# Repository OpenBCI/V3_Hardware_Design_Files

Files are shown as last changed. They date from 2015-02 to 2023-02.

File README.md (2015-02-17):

# V3_Hardware_Design_Files
Contains files created with Design Spark PCB Capture Software

# Installation
Design Spark is a free PCB design software available for download here
http://www.rs-online.com/designspark/electronics/eng/page/designspark-pcb-home-page

Download and install the Design Spark software (Windows based), then follow the instructions below to view, modify, etc.

The OpenBCI board suite uses many custom components that we've designed in Design Spark.
In order to use the design files to their fullest extent, you must add the files contained in the Design Spark Libraries folder to the following location:

    Users\Public\Documents\DesignSpark PCB 7.0\Library\User

Then, fire up Design Spark! If this is your first time running Design Spark, you will need to enable the Library folder first thing. When Design Spark opens, open the Libraries pane by clicking File, Libraries (Cntrl+L). When it opens, click on the Folders tab and select 

    C:\Users\Public\Documents\DesignSpark PCB 7.0\Library 

Then click the 'Folder Enebled' radio button.

Now when you open the .sch and .pcb files, you can modify to your hearts delight!

# License Information

All contents of this repository are released under [Creative Commons Share-alike 3.0](http://creativecommons.org/licenses/by-sa/3.0/).

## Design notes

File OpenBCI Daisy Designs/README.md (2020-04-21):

# OpenBCI Daisy Hardware Design Files

You should have received a copy of the license information for these Open Source hardware files. We are licensing under the [CC-BY-SA 4.0 License](http://creativecommons.org/licenses/by-sa/4.0/legalcode). You should also have downloaded the Design Spark Library files in this directories parent. To get setup with the Design Spark software, go [here.](https://github.com/OpenBCI/V3_Hardware_Design_Files/blob/master/README.md)

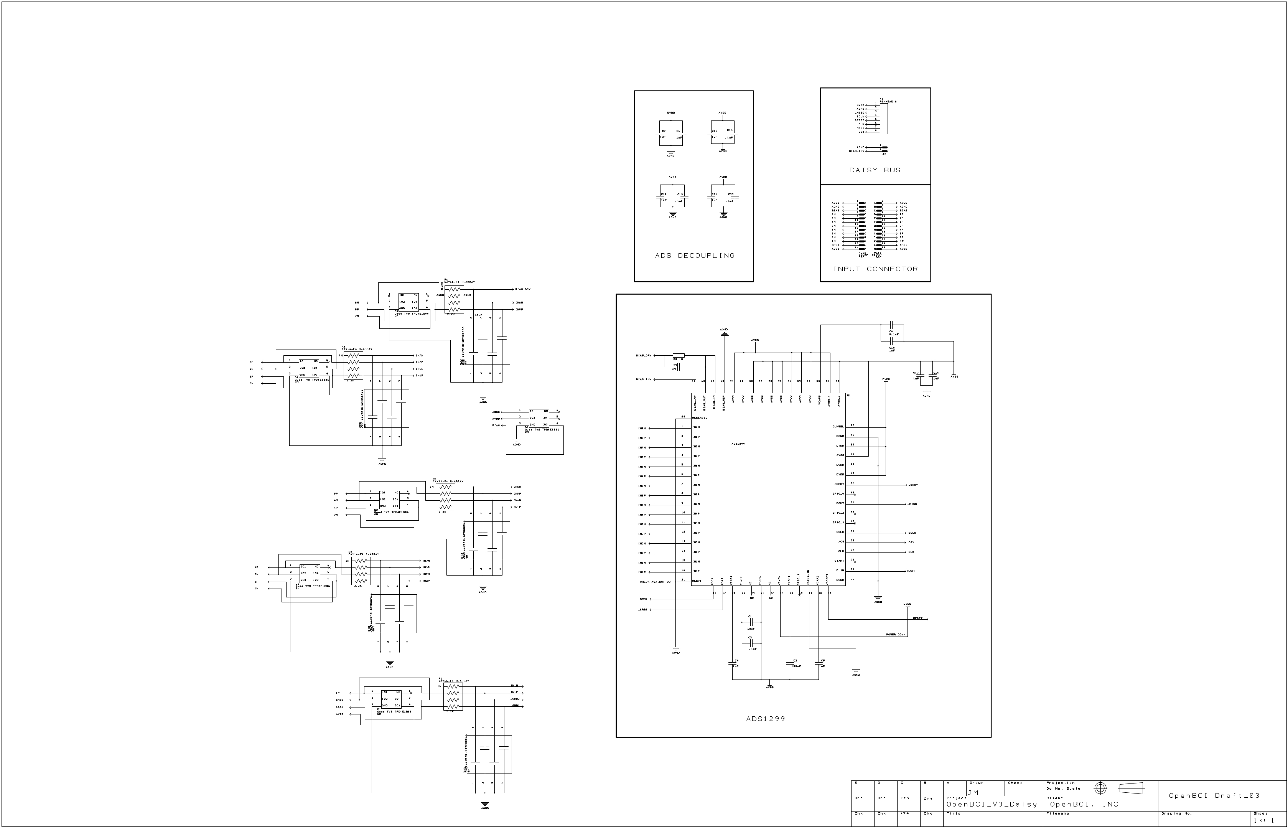
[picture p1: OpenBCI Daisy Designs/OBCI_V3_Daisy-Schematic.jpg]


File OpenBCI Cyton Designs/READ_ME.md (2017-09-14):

# OpenBCI Cyton Hardware Design Files

**NOTE** The OpenBCI **Cyton** used to be called the **32bit Board**. It has be rebranded and there is NO difference between the two.

You should have received a copy of the license information for these Open Source hardware files. We are licensing under the [CC-BY-SA 4.0 License](http://creativecommons.org/licenses/by-sa/4.0/legalcode). You should also have downloaded the Design Spark Library files in this directories parent. To get setup with the Design Spark software, go [here.](https://github.com/OpenBCI/V3_Hardware_Design_Files/blob/master/README.md)

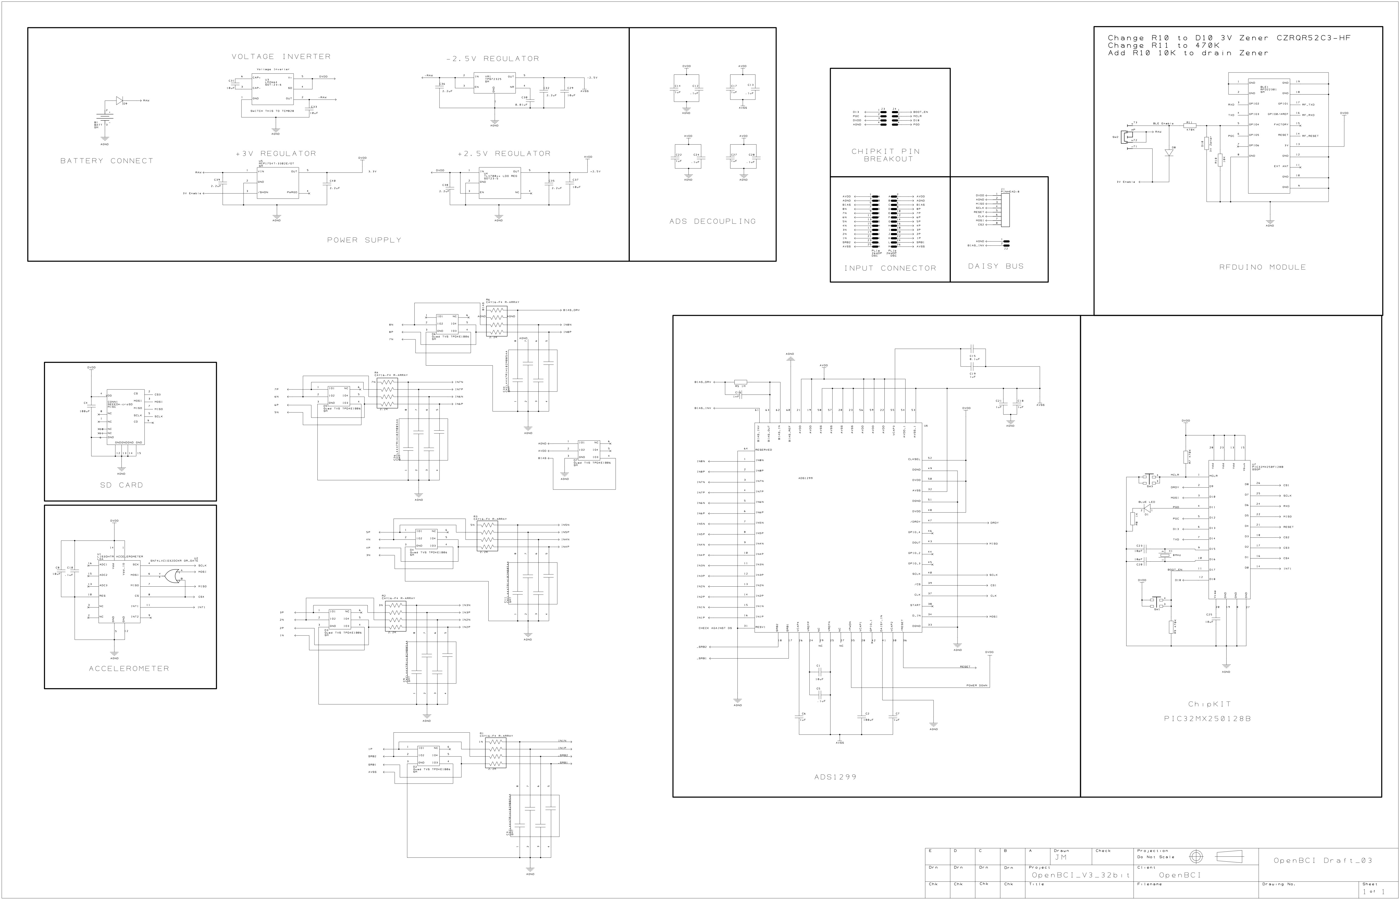
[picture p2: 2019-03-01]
OpenBCI Cyton Designs/OBCI_V3_32bit-Schematic.jpg

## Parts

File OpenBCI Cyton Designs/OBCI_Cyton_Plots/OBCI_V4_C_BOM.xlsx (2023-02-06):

 | OBCI_V3_C
Item | Board Ref | Qty | Component | Value | Package | Manufacturer | Part Number | Description
1 | C2,C4 | 2 | C | 100uF | SM 1206 | Yageo | CC1206MKX5R5BB107 | MLCC
2 | C1,C8,C25,C29,C31,C33,C37 | 7 | C | 10uF | SM0603 | Murata | GRM188C80G106KE47D | MLCC
3 | C32,C35,C36,C38,C40 | 5 | C | 2.2uF | EIA_0402 | Murata | GRM155C80J225ME95D | MLCC
4 | C39 | 1 | C | 2.2uF | EIA_0402 | Murata | GRM155R61C225KE44D | MLCC
5 | C6,C7,C14,C17,C18,C19,C21,C22,C27 | 9 | C | 1uF | EIA_0402 | Yageo | CC0402KRX7R5BB105 | MLCC
6 | C5,C10,C12,C13,C15,C24,C28 | 7 | C | 0.1uF | EIA_0402 | Yageo | CC0402KRX7R7BB104 | MLCC
7 | C30 | 1 | C | 0.01uF | EIA_0402 | Yageo | CC0402KRX7R7BB103 | MLCC
8 | C16 | 1 | C | 0.001uF | EIA_0402 | Yageo | CC0402KRX7R7BB102 | MLCC
9 | C20,C23 | 2 | C | 18pF | EIA_0402 | Yageo | CC0402JRNPO9BN180 | MLCC
10 | R1,R2,R3,R4,R6 | 5 | R | 2.2K | SM | BOURNS | CAY16-2201F4LF | 4 R-ARRAY
11 | C3,C9,C11,C26,C34 | 5 | C | 0.001uF | SM | TDK | CKCL44X7R1H102M085AA | 4 CAP ARRAY
12 | U1 | 1 | U |  | LGA | ST | LIS3DHTR | ST ACCELEROMETER
13 | U2 | 1 | U |  | SM | TI | SN74LVC1G32DCKR | OR_GATE
14 | U3 | 1 | U |  | SOT-23-6 | TI | LM2664M6/NOPB | V INVERTER
15 | U4 | 1 | U |  | SOT-23-5 | TI | TLV70025QDDCRQ1 | +2.5V LDO REG
16 | U5 | 1 | U |  | SM | Microchip | MCP1754T-3302E/OT | 3V3 LDO REG
17 | U6 | 1 | U |  | TQFP-64 | TI | ADS1299IPAG | ADS1299
18 | U7 | 1 | U |  | SSOP-28 | Microchip | PIC32MX250F128B-I/SS | PIC32 MICROCONTROLLER
19 | VR1 | 1 | VR |  | SM | TI | TPS72325DBVR | -2.5 LDO REG
20 | BLE1 | 1 | BLE |  | SM | RF DIGITAL | RFD22301 | BTLE Module
21 | D1 | 1 | D | LED | SM 0603 | Lite-On | LTST-C193TBKT-5A | BLUE LED
22 | D8 | 2 | D |  | SM 0603 | Comchip | CDSU400B | DIODE
23 | D9 | 1 | D |  | SM 0603 | Comchip | CDBU0130L | DIODE
24 | D2,D3,D4,D5,D6,D7 | 6 | D |  | SM | TI | TPD4E1B06DCKR | TI QUAD TVS
25 | D10 | 1 | D | 3V | SOD-923 | Comchip | CZRQR52C3-HF | 3V Zener Diode
26 | R8,R10,R11 | 3 | R | 1K | EIA_0402 | Yageo | RT0402FRE071KL | Resistor
27 | R5 | 1 | R | 1M | EIA_0402 | Yageo | RC0402JR-071ML | Resistor
28 | R7,R9 | 2 | R | 470K | EIA_0402 | Yageo | RC0402JR-07470KL | Resistor
29 | X1 | 1 | X | 8MHz | SM | ABRACON | ABMM2-8.000MHZ-E2-T | 8MHz XTAL
30 | B1 | 1 | BATT |  | SM | JST Sales | S2B-PH-SM4-TB(LF)(SN) | CONN HEADER PH SIDE 2POS 2MM SMD
31 | SW2 | 1 | S |  | SM | COPAL | CUS-13TB | SP3T SLIDE SWITCH
32 | SW1,SW3 | 2 | S |  | SM | C&K | PTS810 SJK 250 SMTR LFS | TACT SWITCH
33 | CONN1 | 1 | CONN |  | SM | SUNTECH | ST-TF-003A | microSD card slot
34 | PL1 | 1 | J |  | DIP | Wurth | 61302221021 | Dual 11 x 2 0.1" pitch MALE header row Right Angle

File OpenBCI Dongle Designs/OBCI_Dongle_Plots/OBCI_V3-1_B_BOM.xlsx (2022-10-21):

 | OBCI_V3_B
Item | Board Ref | Qty | Component | Value | Package | Manufacturer | Part Number | Description
1 | U1 | 1 | FT231X |  | QFN-20 | FTDI | FT231XQ-R | FTDI VCP
2 | BLE1 | 1 | Rfduino |  | SM | Rfdigital | RFD22301 | BTLE Module
3 | D1,D2 | 2 | ESD_VARISTOR |  | SM_0402 | BOURNS | CG0402MLC-05LG | tsv varistor
4 | D3 | 1 | TVS_D |  | SOD882 | ST | ESDALC6V1-1M2 | transient suppressor
5 | D6 | 1 | SMT_LED | BLUE | SM_0603 | Lite-On | LTST-C193TBKT-5A | BLUE LED
6 | D5 | 1 | SMT_LED | GREEN | SM_0603 | Lite-On | LTST-C191KGKT | GREEN LED
7 | D4 | 1 | SMT_LED | RED | SM_0603 | Lite-On | LTST-C191KRKT | RED LED
8 | L1,L2 | 2 | CHOKE |  | SM_0402 | TDK | MPZ1005S300C | FERRITE CHIP
9 | F1 | 1 | SM_FUSE |  | SM_1812 | BOURNS | MF-MSMF050-2 | FUSE
10 | R6,R7 | 2 | R 0402 | 1K | EIA_0402 | Yageo | RT0402FRE071KL | CHIP RESISTOR
11 | R1,R2 | 2 | R 0402 | 22 Ohm | EIA_0402 | Yageo | RC0402FR-0722RL | CHIP RESISTOR
12 | R3,R4,R5 | 3 | R 0402 | 330 Ohm | SM_0402 | Yageo | RC0402JR-07330RL | CHIP RESISTOR
13 | C1,C5, C6 | 3 | C | 0.01uF | EIA_0402 | Yageo | CC0402KRX7R7BB103 | MLCC X7R
14 | C2,C3 | 2 | C | 47pF | SM_0402 | Murata | GRM0335C1E470JA01D | MLCC X7R
15 | C4 | 1 | C 10uF | 10uF | SM0603 | Murata | GRM188C80G106KE47D | MLCC X7R
16 | S1 | 1 | SMT_SPDT_Switch |  | SM | ALPS | SSSS811101 | SPDT SLIDE SWITCH
17 | R8, R9 | 2 | R 0402 | 10K | SM_0402 | Yageo | RC0402JR-07330RL | CHIP RESISTOR

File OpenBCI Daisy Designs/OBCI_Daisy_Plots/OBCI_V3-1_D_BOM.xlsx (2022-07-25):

 | OBCI_V3_D
Item | Board Reference | Qty | Component | Value | Package | Manufacturer | Part Number | Description
1 | U1 | 1 | U |  | TQFP-64 | TI | ADS1299IPAG | ADS1299
2 | D1,D2,D3,D4,D5,D6 | 6 | D |  | SM | TI | TPD4E1B06DCKR | QUAD TVS
3 | C2 | 1 | C | 100uF | SM 1206 | Yageo | CC1206MKX5R5BB107 | Capacitor, Surface Mount Multi-Layer Ceramic
4 | C1 | 1 | C | 10uF | SM0603 | Murata | GRM188C80G106KE47D | Capacitor, Surface Mount Multi-Layer Ceramic
5 | C3,C6,C8,C14,C19,C22 | 6 | C | 0.1uF | EIA_0402 | Yageo | CC0402KRX7R7BB104 | Capacitor, Surface Mount Multi-Layer Ceramic
6 | C9 | 1 | C | 0.001uF | EIA_0402 | Yageo | CC0402KRX7R7BB102 | Capacitor, Surface Mount Multi-Layer Ceramic
7 | C4,C5,C7,C10,C15,C16,C17,C18,C21 | 9 | C | 1uF | EIA_0402 | Yageo | CC0402KRX7R5BB105 | Capacitor, Surface Mount Multi-Layer Ceramic
8 | C11,C12,C13,C20,C23 | 5 | C | 0.001uF | SM | TDK | CKCL44X7R1H102M085AA | 4 CAPACITOR ARRAY
9 | R1,R2,R3,R4,R6 | 5 | R | 2.2K | SM | BOURNS | CAY16-2201F4LF | 4 R-ARRAY
10 | R5 | 1 | R | 1M | EIA_0402 | Yageo | RC0402JR-071ML | Resistor
11 | PL1 | 1 | J |  | DIP | Wurth | 61302221021 | Dual 11 x 2 0.1" pitch MALE header row Right Angle

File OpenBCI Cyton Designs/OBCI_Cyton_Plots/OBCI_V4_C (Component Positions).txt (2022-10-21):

Component Positions Report
--------------------------

Report File:    C:\Users\murf\Documents\SPARK\ADS_EEG\ADS_V3_BT\OBCI_C\OBCI_V4_C (Component Positions).txt
Report Written: Friday, August 12, 2016
Design Path:    C:\Users\murf\Documents\SPARK\ADS_EEG\ADS_V3_BT\OBCI_C\OBCI_V4_C.pcb
Design Title:
Created:        7/30/2013 10:43:11 PM
Last Saved:     8/12/2016 11:11:35 AM
Editing Time:   116245 min
Units:          thou (precision 0)

Name      Component                     Side                    Centre X    Centre Y  Rotation
----------------------------------------------------------------------------------------------
J2        2WP                           Top                         1611        1483    180.00
J3        4WP                           Top                         1912         375    315.00
J4        4WP                           Top                         2104         739      0.00
PL1       26WDP                         Top                         1217        2119    270.00
C1        0603YC104KATDA                Top                          784        1422    270.00
C8        0603YC104KATDA                Top                          881         174    180.00
C25       0603YC104KATDA                Bottom                      1251         870     90.00
C29       0603YC104KATDA                Bottom                      1373        1138    270.00
C31       06033G104ZATDA                Bottom                      1349         768    180.00
C33       06033G104ZATDA                Bottom                      1464         921    270.00
X1        ABRACON_XTAL                  Top                         1672         795    270.00
U6        ADS1299                       Top                         1172        1403    270.00
B1        BATT                          Bottom                      1993        1477    180.00
C5        C                             Top                          873        1433    180.00
C6        C                             Top                          846        1370    270.00
C7        C                             Top                          846        1236    270.00
C10       C                             Top                          941         186    180.00
C12       C                             Top                         1351        1108     90.00
C13       C                             Bottom                      1125        1450      0.00
C14       C                             Top                         1351        1068     90.00
C15       C                             Top                         1473        1404      0.00
C16       C                             Top                         1508        1550      0.00
C17       C                             Bottom                      1163        1450      0.00
C18       C                             Bottom                      1181        1386    270.00
C19       C                             Top                         1509        1404      0.00
C20       C                             Top                         1646         949     90.00
C21       C                             Bottom                      1181        1348    270.00
C22       C                             Bottom                      1201        1450      0.00
C23       C                             Top                         1700         643    270.00
C24       C                             Bottom                      1239        1450      0.00
C27       C                             Bottom                      1299        1430    270.00
C28       C                             Bottom                      1299        1392    270.00
C30       C                             Bottom                      1356         923     90.00
C32       C                             Bottom                      1480        1128     90.00
C35       C                             Bottom                      1561        1127    270.00
C36       C                             Bottom                      1560        1042    180.00
C38       C                             Bottom                      1830        1092      0.00
C39       C                             Bottom                      1917        1006     90.00
C40       C                             Bottom                      1916         758     90.00
C37       C 10uF                        Bottom                      1618        1186    270.00
C2        C 100uF                       Top                          771        1307     90.00
C4        C 100uF                       Bottom                       789         196    315.00
R1        CAY16-F4 R-ARRAY              Top                          796        1843    180.00
R2        CAY16-F4 R-ARRAY              Top                          988        1842    180.00
R3        CAY16-F4 R-ARRAY              Top                         1180        1843    180.00
R4        CAY16-F4 R-ARRAY              Top                         1372        1842    180.00
R6        CAY16-F4 R-ARRAY              Top                         1566        1842    180.00
LOGO1     CHIPKIT                       Top                         1414         454      0.00
C3        CKCL44X7R1H102M085AA          Bottom                       794        1645      0.00
C9        CKCL44X7R1H102M085AA          Bottom                       998        1645      0.00
C11       CKCL44X7R1H102M085AA          Bottom                      1176        1645      0.00
C26       CKCL44X7R1H102M085AA          Bottom                      1352        1645      0.00
C34       CKCL44X7R1H102M085AA          Bottom                      1540        1645      0.00
SW2       CUS-3B SP3T SLIDE SWITCH      Bottom                      2341        1196     90.00
D1        DI0603                        Top                         1810         702      0.00
D8        DI0603                        Top                         2247        1261      0.00
D9        DI0603                        Bottom                      1992        1111    180.00
U1        LIS3DHTR ACCELEROMETER        Top                          885         312    180.00
U3        LM2664                        Bottom                      1459         784    180.00
U5        LP5907                        Bottom                      1935         879    180.00
U7        PIC32MX250F128B               Top                         1321         780     90.00
J1        PINHEAD-8                     Top                          543        1205    315.00
D2        Quad TVS TPD4E1B06            Bottom                       769        1961      0.00
D3        Quad TVS TPD4E1B06            Bottom                       963        1963      0.00
D4        Quad TVS TPD4E1B06            Bottom                      1165        1967      0.00
D5        Quad TVS TPD4E1B06            Bottom                      1363        1969      0.00
D6        Quad TVS TPD4E1B06            Bottom                      1563        1971      0.00
D7        Quad TVS TPD4E1B06            Bottom                      1765        1973      0.00
D10       R                             Bottom                      2152        1098      0.00
R5        R                             Top                         1471        1549    180.00
R7        R                             Top                         1808         914      0.00
R8        R                             Top                         1863         708      0.00
R9        R                             Top                         1927        1467    270.00
R10       R                             Top                         2195        1101    180.00
R11       R                             Bottom                      2197        1098    180.00
BLE1      RFD22301                      Bottom                      1400         305      0.00
CONN1     SEEEDmicroSD                  Bottom                       564         561    315.00
PL2       SMT_QUAD_04                   Bottom                       308        1237    135.00
U2        SN74LVC1G32DCKR OR_GATE       Top                         1000         565      0.00
SW1       SW_TACT                       Top                         1905        1331      0.00
SW3       SW_TACT                       Top                         1909        1002    180.00
U4        TLV700xx LDO REG              Bottom                      1711        1072     90.00
VR1       TPS72325                      Bottom                      1436        1027     90.00
----------------------------------------------------------------------------------------------

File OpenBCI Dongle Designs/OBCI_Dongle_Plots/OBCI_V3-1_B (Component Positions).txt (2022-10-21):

Component Positions Report
--------------------------

Report File:    C:\Users\murf\Documents\SPARK\ADS_EEG\ADS_V3_BT\OBCI_B\OBCI_V3_B (Component Positions).txt
Report Written: Thursday, December 10, 2015
Design Path:    C:\Users\murf\Documents\SPARK\ADS_EEG\ADS_V3_BT\OBCI_B\OBCI_V3_B.pcb
Design Title:
Created:        6/17/2014 9:28:35 AM
Last Saved:     12/10/2015 11:56:17 AM
Editing Time:   3459 min
Units:          thou (precision 0)

Name      Component                     Side                    Centre X    Centre Y  Rotation
----------------------------------------------------------------------------------------------
C1        C                             Top                          559         345    180.00
C2        C                             Top                          650         576     90.00
C3        C                             Top                          650         411     90.00
C5        C                             Top                         1465          69     90.00
C6        C                             Top                         1175         224    270.00
C4        C 10uF                        Top                         1545         865    270.00
J1        CONN-5                        Top                          785          60    180.00
J2        CONN_7                        Top                          885         865    180.00
D1        ESD_VARISTOR                  Top                          650         631     90.00
D2        ESD_VARISTOR                  Top                          650         360     90.00
U1        FT231X                        Top                          925         500    270.00
L1        MPZ1005S300C                  Top                          560         645    180.00
L2        MPZ1005S300C                  Top                          610         255    180.00
R1        R 0402                        Top                          651         519    270.00
R2        R 0402                        Top                          651         459    270.00
R3        R 0402                        Top                          901         669    270.00
R4        R 0402                        Top                          996         354    270.00
R5        R 0402                        Top                         1331         304     90.00
R6        R 0402                        Top                         1335         576     90.00
R7        R 0402                        Top                         1336         534    270.00
R8        R 0402                        Top                         1720         836     90.00
R9        R 0402                        Top                         1760         881     90.00
BLE1      RFD22301                      Top                         1705         464     90.00
D4        SMT_LED                       Top                         1015         670     90.00
D5        SMT_LED                       Top                         1015         295     90.00
D6        SMT_LED                       Top                         1305         355     90.00
S1        SMT_SPDT_Switch               Top                         1225         107      0.00
F1        SM_FUSE                       Top                          760         245      0.00
D3        TVS_D                         Top                          846         340    180.00
CONN1     USB_PCB                       Top                          225         463     90.00
----------------------------------------------------------------------------------------------

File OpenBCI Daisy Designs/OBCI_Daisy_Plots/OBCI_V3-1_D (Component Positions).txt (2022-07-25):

Component Positions Report
--------------------------

Report File:    C:\Users\murf\Documents\SPARK\ADS_EEG\ADS_V3_BT\OBCI_D\OBCI_V3_D (Component Positions).txt
Report Written: Thursday, December 10, 2015
Design Path:    C:\Users\murf\Documents\SPARK\ADS_EEG\ADS_V3_BT\OBCI_D\OBCI_V3_D.pcb
Design Title:
Created:        7/30/2013 9:43:11 PM
Last Saved:     9/24/2015 12:07:36 PM
Editing Time:   113404 min
Units:          thou (precision 0)

Name      Component                     Side                    Centre X    Centre Y  Rotation
----------------------------------------------------------------------------------------------
J2        2WP                           Top                         1613         663    180.00
PL1       26WDP                         Top                         1219        1261    270.00
C1        0603YC104KATDA                Top                          786         564    270.00
U1        ADS1299                       Top                         1174         545    270.00
C3        C                             Top                          875         575    180.00
C4        C                             Top                          848         512    270.00
C5        C                             Top                          848         378    270.00
C6        C                             Top                         1353         250     90.00
C7        C                             Top                         1353         210     90.00
C8        C                             Top                         1475         546      0.00
C9        C                             Top                         1510         692      0.00
C10       C                             Top                         1511         546      0.00
C14       C                             Bottom                      1127         592      0.00
C15       C                             Bottom                      1165         592      0.00
C16       C                             Bottom                      1183         528    270.00
C17       C                             Bottom                      1183         490    270.00
C18       C                             Bottom                      1203         592      0.00
C19       C                             Bottom                      1241         592      0.00
C21       C                             Bottom                      1301         572    270.00
C22       C                             Bottom                      1301         534    270.00
C2        C 100uF                       Top                          773         449     90.00
R1        CAY16-F4 R-ARRAY              Top                          788         985    180.00
R2        CAY16-F4 R-ARRAY              Top                          983         985    180.00
R3        CAY16-F4 R-ARRAY              Top                         1182         985    180.00
R4        CAY16-F4 R-ARRAY              Top                         1383         985    180.00
R6        CAY16-F4 R-ARRAY              Top                         1568         985    180.00
C11       CKCL44X7R1H102M085AA          Bottom                       794         794      0.00
C12       CKCL44X7R1H102M085AA          Bottom                      1003         794      0.00
C13       CKCL44X7R1H102M085AA          Bottom                      1178         794      0.00
C20       CKCL44X7R1H102M085AA          Bottom                      1353         794      0.00
C23       CKCL44X7R1H102M085AA          Bottom                      1528         794      0.00
J1        PINHEAD-8                     Top                          545         347    315.00
D1        Quad TVS TPD4E1B06            Bottom                       771        1103      0.00
D2        Quad TVS TPD4E1B06            Bottom                       965        1105      0.00
D3        Quad TVS TPD4E1B06            Bottom                      1167        1109      0.00
D4        Quad TVS TPD4E1B06            Bottom                      1365        1111      0.00
D5        Quad TVS TPD4E1B06            Bottom                      1565        1113      0.00
D6        Quad TVS TPD4E1B06            Bottom                      1767        1115      0.00
R5        R                             Top                         1473         691    180.00
----------------------------------------------------------------------------------------------

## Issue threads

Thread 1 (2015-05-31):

OpenBCI/V3_Hardware_Design_Files #1: Interference on DAISY_SS (D3)

mikeanthonywild, 2015-05-31:
I've been trying to alter the firmware to use the daisychain header to transfer sample to another device via SPI. I've noticed that DAISY_SS picks up a lot of interference from the other SPI lines. Attached is a scope trace of the SPI lines when running unmodified firmware while capturing data from the ADS1299 - note channel 3 (DAISY_SS) is picking up significant interference from the other SPI lines.

[image]

biomurph, 2015-06-01:
Hi mikeanthonywild. Do you have anything attached to the DAISY_SS pin? What board are you using, the 32bit or the 8bit. 
### If you are using the 8bit Board:
The 8bit Board does not touch the DAISY_SS pin in the Library firmware at all, so it is left floating, and you are likely seeing cross-talk on that pin. Try adding this in your setup() and reprogram the board.

  pinMode(DAISY_SS, OUTPUT); 
  digitalWrite(DAISY_SS, HIGH);

### If you are using the 32bit Board:
Well, that's pretty messed up, because the 32bit Board does make the DAISY_SS pin OUTPUT and sets it HIGH so it really should be stable.

mikeanthonywild, 2015-06-01:
Sorry I should have specified, I'm using the 32-bit board. The only thing I have connected to DAISY_SS is a logic analyser. I should add that the trace above, I had set DAISY_SS low as a sanity check. The problem still persists with the default code, except the DC offset is high.

As an aside, I noticed this inconsistency while looking through the code:
    csLow(ADS_SS);        //  open SPI
    xfer(opcode1);          //  Send WREG command & address
    xfer(_numRegistersMinusOne);  //  Send number of registers to read -1
    for (int i=_address; i <=(_address + _numRegistersMinusOne); i++){
        xfer(regData[i]);     //  Write to the registers
    }
    digitalWrite(CS,HIGH);        //  close SPI

biomurph, 2015-06-01:
Well, that is certainly a bug, Thanks for pointing it out. 
It has no effect on the current functionality, because we are not using the WREGS function in our code.
I will fix it, in case others want to use it in future.

I will be pulling my oscope out soon, and take a look at the behavior of the DAISY_SS to see if I can replicate your results.

biomurph, 2015-06-01:
I just scoped a couple of boards here in the OpenBCI lab.
Both 32Bit Boards. The image below Is what I got for both. 
Channel 1 is connected to the CS2 pin on the Daisy Bus. 
Channel 2 is connected to the SCLK pin on the Daisy Bus.
I do see alittle bit of noise in the CS2, but it is certainly acceptable.
Not sure where your noise is coming from. Can you describe your setup?

[image]

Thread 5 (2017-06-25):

OpenBCI/V3_Hardware_Design_Files #5: missing PL2 connector in the schematic but still on the pcb

shadowphile, 2017-06-25:
In the past I downloaded the schematic and it had two pages.  In order to make life easier I merged the two pages together.
After doing my own layout in a different schematic CAD while using the DesignSpark schematic as a reference, I came across something wrong.   I thought I had accidentally erased something when I deleted the second page.
So I erased everything, uninstalled DesignSpark, cleaned out all the residual references like in the registry, then reinstalled DesignSpark (8) and re-downloaded the Cyton files.
Now there is only one page of schematic and it does not contain PL2 even though it is on the PCB.
Now I'm afraid I might be missing other stuff that won't make it onto my own PCB if the official schematic is not complete.
thanks

biomurph, 2017-06-26:
There should be only one page in the schematic.
You may need to make a project, and then put the files into it.
I don't see PL2. What are you referring to?

shadowphile, 2017-06-26:
The pcb in SparkDesign has a PL2 in the Goto list.  Four pads on the
backside, see attached picture.  They are tied to the RFArduino as RFRX and
RFTX and RFRST but on the schematic those lines go nowhere else.
thanks

joelSensor, 2017-06-27:
Oh,
I think I made those SMT pads inside the PCB layout window. I don't think that there is a schematic part for them. You can make pads, place them, and assign nets to them in the pcb layout.

shadowphile, 2017-07-07:
ok, thanks.  as long as those RFRX and RFTX lines aren't used for anything.

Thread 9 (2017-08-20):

OpenBCI/V3_Hardware_Design_Files #9: Daisy module broken or fixed in repo?

ak1n, 2017-08-20:
Does the current daisy module design (which I have already gotten fabbed...) include corrections re the initial design error per here: http://openbci.com/community/daisy-module-re-work/ or do I still need to get the pin corrected? Thanks!

biomurph, 2017-08-21:
This issue was fixed, and this repo should reflect that.
I have migrated from Windows to MAC a couple of years ago. Will verify when in front of a Windows machine. The pin in question is the CLKSEL, pin 52, and it should be pulled to GND so that the Daisy will accept the external CLK signal.

ak1n, 2017-08-26:
Awesome. Thank you for your response, it is appreciated.

Frederik-D-Weber, 2019-06-17:
I checked the design files with DesignSpark. They are still _not_ fixed! The issue remains.

It is more than 4.5 years later.  In the design files, the pin 52 of the ADS199 is still connected to DVDD and not to AGND as is should be. Given the 1) issues this causes, 2) mulitple requests by the community to fix the files, 3) the effort that went into decribing this fix, 4) leaving the impression here that it is fixed... it is not acceptable to have the faulty version on github. Obviously a fixed version exists, since it is used it for the new batches sold on the OpenBCI shop.

Please fix this asap, or I will fork a fixed version.

retiutut, 2022-07-25:
Thanks @tharun-OpenBCI for https://github.com/OpenBCI/V3_Hardware_Design_Files/pull/16

closed 2022-07-25 by retiutut

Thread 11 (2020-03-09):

OpenBCI/V3_Hardware_Design_Files #11: Schematic question——BIASOUT should feedback to bias_INV?

trzp, 2020-03-09:
Hello:
I have read the ads1299 document and the cython's schematic, I found that in the ads1299 document, the "bias drive" output signal (pin63 biasout) is feedback to BIAS_INV pin , however, in the cython's schematic the bias drive signal feeds back to BIAS_IN and leave BIAS_INV float. It makes matters? In my understanding, the bias_in pin is used to connect 'BIASOUT' and a special input channel electrode with proper register configuration. So, I think whether the BIASOUT should feedback to BIAS_INV, and maybe connect the BIAS_IN to ground?

R0dri, 2020-05-14:
I recently came across with this same issue. What I gather:
- BIAS_IN is at the input multiplexer that can be mapped to any channel similar to SRB1, SRB2.
- BIAS_OUT is bridged to BIAS_IN in case you want to see what is the signal from the Bias Amplifier
- BIAS_INV is mapped to the daisy bus. Look ahh Figure 39 from the data sheet to understand why.

If you bridge BIAS_INV with BIAS_OUT you will set the integrated Bias amplifier as a buffer (signal follower). This will let you measure the precise common mode noise present. The config running on board tells me they intend to have the Bias drive amplifier (pin BIAS on the board) to be the amplified difference between the ground plane and the common mode noise collected by the PGAs array. This will effectively send an inverse signal of the common mode noise to be feed to the body. The driver is left open so this signal is as strong as the driver can amplify it in an attempt cancel the noise present. Since the noise levels are commonly very low in magnitude, saturation of the amplifier is not a concern. Are you familiar with the Driven-Right Leg circuit?

Anyhow, I guess you can still connect a jumper wire between BIAS pin and BIAS_INV on the board to accomplish the voltage follower proposed by the data sheet as you mentioned.

Here is the data sheet for reference:
(http://www.ti.com/lit/ds/symlink/ads1299.pdf)

JoshQuint, 2023-04-11:
You might also be interested in these discussions regarding the same topic:
- [TI forum](https://e2e.ti.com/support/data-converters-group/data-converters/f/data-converters-forum/424183/ads1299-bias-setting)
- [OpenBci forum](https://openbci.com/forum/index.php?p=/discussion/2917/bias-pinout)

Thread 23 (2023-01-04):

OpenBCI/V3_Hardware_Design_Files #23: How to open .sch or .pcb file in EAGLE

shubhankar9, 2023-01-04:
Hi, I wanted to convert this design to a single or two layered PCB. I am comfortable using EAGLE and so I wanted to open the 32bit .pcb and .sch files in EAGLE. I can't seem to find a way to do that. I am able to open and view it in DesignSpark but there is not export option that makes these files compatible with EAGLE. Would love your thoughts on this.

JoshQuint, 2023-03-14:
As I had the same problem I can tell you that DesignSpark and Eagle files are not compatible. 
I could not find any tools that would allow you to import them yet.
Therefor, if you want to stick to Eagle, you will basically have to use the DesignSpark schematics as a reference to build your own schematic and later design the board in Eagle.
Alternatively, look up open-source hardware projects that might use the same ADC and Eagle.
Also keep a track of the open issues in this repository, in case you consider a different approach for your own project.

shubhankar9, 2023-03-14:
That's interesting. Good to know. Thank you!

Regards
Shubhankar

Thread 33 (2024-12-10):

OpenBCI/V3_Hardware_Design_Files #33: Cyton BOM vs Schematic vs Design Spark Inconsistency Issue

FlywheelMist, 2024-12-10:
Hello,
I was looking through the schematics, BOM, and designspark to find that there are 3 different components and wiring for the R11, R10, D10. This includes R11 resistance value (330k, 470k or 1k), R10 resistance value (10k, 1k, 220k) and the presence of D10 entirely.

Could these please be specified or updated?

Many thanks,
M

Images:

DesignSpark:
[image]

BOM:
[image]

Schematics:
[image]

atulakella, 2025-11-16:
Hey!
Just stumbled across the same issue, I see a lot of inconsistencies in BOM and component position files, did you find a workaround or did you get help from the maintainers of this repo?

FlywheelMist, 2025-11-16:
Hey @atulakella 
Afraid I've long since abandoned this project and don't remember finding a solution... I think your best bet for this is to contact someone from openbci directly... Sorry I can't be of more help.
M

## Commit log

2015-02-17 Initial commit
    initial commit of these files which are PCB .sch and .brd files made
    with Design Spark PCB Capture program
    [OpenBCI 32bit.sch, OpenBCI 8bit.sch, OpenBCI Daisy.sch, OpenBCI Dongle.sch]
2017-06-20 Updated the Design files with re-oriented battery socket
2017-09-14 Updated repo to comply with OSHWA Certification Guidelines
    [OBCI_Cyton_ Component Positions.csv, OBCI_Cyton_BOM.xlsx, OBCI_Cyton_Board Outline.gbr, OBCI_Cyton_Bottom Copper.gbr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]
2022-07-25 Updated Daisy Design Files
    Updated Gerber Files:
    Pin 51 and 52 short removed
    [OBCI_Daisy_Board Outline.gbr, OBCI_Daisy_Bottom Copper.gbr, OBCI_Daisy_Bottom Paste Mask.gbr, OBCI_Daisy_Bottom Solder Mask.gbr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]
2022-07-26 Updated Dongle Gerber/BOM
    [OBCI_Dongle_ Bottom Copper.gbr, OBCI_Dongle_BOM.xlsx, OBCI_Dongle_Board Outline.gbr, OBCI_Dongle_Bottom Paste Mask.gbr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]
2022-10-04 updated cyton gerber files
    [OBCI_Cyton_ Component Positions.csv, OBCI_Cyton_BOM.xlsx, OBCI_Cyton_Board Outline.gbr, OBCI_Cyton_Bottom Copper.gbr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]
2023-02-06 added cyton bom
    [OBCI_V4_C_BOM.xlsx]
